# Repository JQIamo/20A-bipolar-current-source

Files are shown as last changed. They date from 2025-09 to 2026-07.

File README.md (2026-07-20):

# Bias Coils Current Controller
This repo provides information regarding the Bias Coils Current Controller (here on out referred to as “the controller”) used by the Schine Group at the Joint Quantum Institute (JQI) at University of Maryland, College Park. This is an experimental apparatus designed to drive Helmholtz coil pairs to cancel external magnetic fields which would otherwise disturb the experiment. The controller provides an output current proportional to an input voltage and features an ultra-low noise feedback circuit design for precise control of the output current down to the fractional mA level. The controller has three channels to independently control the magnetic fields along the x, y, and z axes.

## 20A-bipolar-current-source
This project is based on the [`20A-bipolar-current-source`](https://github.com/JQIamo/20A-bipolar-current-source/tree/faf83a785aa46d90d6e65fa55f9879bae6bd2d8a) design of Mingshu Zhao and Alessandro Restelli. Details on the circuit can be found in their [research article in AIP Advances](https://doi.org/10.1063/5.0138145).

## Circuit files
There are several KiCad project folders within the `kicad` directory in this repo.
* `controller_board` contains the circuit board for the main controller board on which the analog PI feedback is located.
* `Controller_supply` contains the controller's on-board power supply circuit board (used for powering the controller boards)
* `H-bridge` is for the development of the MOT coil current controller (empty project as of Jun 06, 2024).
* `rear` contains the original, liquid-cooled circuit board design housing the power MOSFETs that control the coil current. (Not used in this controller)
* `SchineLab_CoilFET_Board` contains the modified, air-cooled circuit board design housing the power MOSFETs for coil current control. (Used in this controller)

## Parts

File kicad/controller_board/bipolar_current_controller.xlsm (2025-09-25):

# | Reference | Qty | Value | Footprint | DNP | DIGIKEY PARTNO | MPN
1 | C1, C2, C3, C4, C5, C6, C7, C8, C9, C10, C11, C12, C13, C14, C15, C16, C17, C18, C19, C20, C22, C23, C37, C43, C44, C47, C48 | 27 | 0.1uF | Capacitor_SMD:C_0603_1608Metric |  | 490-14357-1-ND | GCM188R71H104JA57D
2 | C24, C29 | 2 | 10n | Capacitor_SMD:C_0603_1608Metric |  | 445-7404-1-ND | C1608C0G1H103J080AA
3 | C25, C27, C28, C30 | 4 | 1n | Capacitor_SMD:C_0603_1608Metric |  | 1276-1018-1-ND | 1276-1018-1-ND
4 | C31, C32 | 2 | 220uF | zmyfootprint:CAP_polar_220uF |  | PCE4428CT-ND | EEE-FK1V221AP
5 | C33, C34, C39, C40, C49, C51 | 6 | 10uF | Capacitor_SMD:C_1210_3225Metric |  | 445-14933-1-ND | C3225X7R1H106M250AC
6 | C35, C36 | 2 | 47uF | Capacitor_Tantalum_SMD:CP_EIA-7343-43_Kemet-X |  | 399-3905-1-ND | T495X476K035ATE300
7 | C41, C42, C45, C46 | 4 | 0.33uF | Capacitor_SMD:C_0603_1608Metric |  | 445-5950-1-ND | C1608X7R1H334K080AC
8 | C50, C52 | 2 | 1uF | Capacitor_Tantalum_SMD:CP_EIA-3528-21_Kemet-B |  | 399-9720-1-ND | T491B105K050AT
9 | D1, D2, D4, D5 | 4 | D | Diode_SMD:D_MiniMELF |  | 1514-CLL4150TRPBFREECT-ND | CLL4150 TR PBFREE
10 | D3, D6 | 2 | LED | LED_THT:LED_D5.0mm_Horizontal_O3.81mm_Z3.0mm |  | 516-2483-1-ND | HLMP-4700-C0002
11 | H1, H2, H3, H4 | 4 | MountingHole | MountingHole:MountingHole_4mm
12 | J1 | 1 | Error signal | zKiCadFootprints:BNC_Amphenol_B6252HB-NPP3G-50_Horizontal_mount_float |  | A32260-ND | 5227161-7
13 | J2 | 1 | Set point | zKiCadFootprints:BNC_Amphenol_B6252HB-NPP3G-50_Horizontal_mount_float |  | A32260-ND | 5227161-7
14 | J4 | 1 | Monitor | zKiCadFootprints:BNC_Amphenol_B6252HB-NPP3G-50_Horizontal_mount_float |  | A32260-ND | 5227161-7
15 | J5 | 1 | Conn_02x04_Counter_Clockwise | zKiCadFootprints:SSO-8_7.62x10.1mm_P2.54mm_Clearance8mm |  | 1212-1032-ND | 114-87-308-41-134161
16 | J6 | 1 | Enable | zKiCadFootprints:BNC_Amphenol_B6252HB-NPP3G-50_Horizontal_mount_float |  | A32260-ND | 5227161-7
17 | J7 | 1 | N-MOS | Connector_Molex:Molex_KK-254_AE-6410-02A_1x02_P2.54mm_Vertical
18 | J8 | 1 | P-MOS | Connector_Molex:Molex_KK-254_AE-6410-02A_1x02_P2.54mm_Vertical
19 | J9 | 1 | Shunt resistor | Connector_Molex:Molex_KK-254_AE-6410-02A_1x02_P2.54mm_Vertical
20 | L1, L2 | 2 | 100uH | Inductor_SMD:L_TDK_SLF10145 |  | 445-1976-1-ND | SLF10145T-101M1R0-PF
21 | L3, L4 | 2 | 1k | Inductor_SMD:L_0603_1608Metric |  | 445-MMZ1608R102ATA00CT-ND | MMZ1608R102ATA00
22 | P1 | 1 | CONN_01X03 | zmyfootprint:Conn_01X03-3.5mm |  | 277-1722-ND | 1984620
23 | R1, R3, R10 | 3 | 50 | Resistor_SMD:R_0603_1608Metric |  | 764-FC0603E50R0BTBST1CT-ND | FC0603E50R0BTBST1
24 | R2 | 1 | 200 | Resistor_SMD:R_0603_1608Metric |  | RNCF0603TKY200RCT-ND | RNCF0603TKY200R
25 | R4 | 1 | 1M | Resistor_SMD:R_0603_1608Metric |  | YAG4498CT-ND | RT0603BRD071ML
26 | R5 | 1 | DNP | Resistor_SMD:R_0805_2012Metric
27 | R6 | 1 | 1k | Resistor_SMD:R_0805_2012Metric |  | RG2012V1.0KPCT-ND | RNCF0805TKY1K00
28 | R7 | 1 | R_Shunt |  |  | 804-1050-ND | Y09430R01000F9L
29 | R8, R11 | 2 | 25k | Resistor_SMD:R_2512_6332Metric |  | 804-1122-1-ND | Y174525K0000T9R
30 | R9, R12 | 2 | 500 | Resistor_SMD:R_2512_6332Metric |  | Y1121-500CT-ND | Y1121500R000T9R
31 | R13, R15, R17, R18 | 4 | 18.2k | Resistor_SMD:R_0805_2012Metric |  | 2019-RK73H2ATTD1822FCT-ND | RK73H2ATTD1822F
32 | R14, R16, R19, R20 | 4 | 2.2k | Resistor_SMD:R_0805_2012Metric |  | 749-1728-1-ND | MCU08050C2201FP500
33 | R22, R23 | 2 | 1 | Resistor_SMD:R_0603_1608Metric |  | RNCP0603FTD1R00CT-ND | RNCP0603FTD1R00
34 | R25, R26 | 2 | DNP | Resistor_SMD:R_0603_1608Metric
35 | R27, R28 | 2 | 33 | Resistor_SMD:R_0603_1608Metric |  | 311-33.0HRCT-ND | RC0603FR-0733RL
36 | R31, R32, R39 | 3 | 1k | Resistor_SMD:R_0603_1608Metric |  | RNCP0603FTD1K00CT-ND | RNCP0603FTD1K00
37 | R33, R34 | 2 | 1.8k | Resistor_SMD:R_0603_1608Metric |  | 764-1393-1-ND | PTN0603E1801BST1
38 | R35, R36, R37, R38 | 4 | 120 | Resistor_SMD:R_0603_1608Metric |  | RG16P120BCT-ND | RG1608P-121-B-T5
39 | R40, R41 | 2 | 30m | Resistor_SMD:R_1206_3216Metric |  | 4463-D1WEL1206MR033F-T5CT-ND | D1WEL1206MR033F-T5
40 | RV1, RV2 | 2 | 1k | Potentiometer_THT:Potentiometer_Bourns_3296W_Vertical |  | 3296W-102LF-ND | 3296W-1-102LF
41 | S1, S2 | 2 | MAX4656 | zKiCadFootprints:MAX4656ESA+ |  | MAX4656ESA+-ND | MAX4656ESA+
42 | TP1 | 1 | TestPoint_Small | RF_Shielding:Laird_Technologies_BMI-S-210-F_44.00x30.50mm |  | 903-1057-1-ND and 903-1020-ND | BMI-S-210-F and BMI-S-210-C
43 | U1, U2, U3 | 3 | AD8421 | zKiCadFootprints:AD8421ARZ-R7 |  | AD8421ARZ-R7CT-ND | AD8421ARZ-R7
44 | U4 | 1 | OPA388 | zKiCadFootprints:OPA388IDR |  | 296-45348-1-ND | OPA388IDR
45 | U5, U6 | 2 | LT1363 | zKiCadFootprints:LT1363CS8#TRPBF |  | 505-LT1363CS8#TRPBFCT-ND | LT1363CS8#TRPBF
46 | U7, U8 | 2 | BUF634A | zKiCadFootprints:TI_SO-PowerPAD-8_ThermalVias |  | 296-BUF634AIDDARCT-ND | BUF634AIDDAR
47 | U11 | 1 | LM338 | Package_TO_SOT_THT:TO-220-3_Vertical |  | LM338T/NOPB-ND | LM338T/NOPB
48 | U12 | 1 | LM337_TO220 | Package_TO_SOT_THT:TO-220-3_Vertical |  | 497-1585-5-ND | LM337SP
49 | U13 | 1 | LM7915 | Package_TO_SOT_SMD:TO-263-2 |  | MC7915ACD2TGOS-ND | MC7915ACD2TG
50 | U14 | 1 | uA7815 | Package_TO_SOT_SMD:TO-252-2 |  | BA7815FP-E2CT-ND | BA7815FP-E2
51 | U15 | 1 | LM7905 | Package_TO_SOT_SMD:TO-263-2 |  | 497-1214-1-ND | L7905CD2T-TR
52 | U16 | 1 | LM7805 | Package_TO_SOT_SMD:TO-263-3_TabPin2 |  | 296-20796-1-ND | UA7805CKTTR
53 | U17 | 1 | TL1963A | zKiCadFootprints:TL1963ADCQR |  | 296-25119-1-ND | TL1963ADCQR
54 | U18 | 1 | LM337_TO220 | Package_TO_SOT_SMD:TO-263-3_TabPin2 |  | 296-20746-1-ND | LM337KTTR
55 | U19 | 1 | FOD8482TR2 | Package_SO:SSO-6_6.8x4.6mm_P1.27mm_Clearance8mm |  | 488-FOD8482TR2CT-ND | FOD8482TR2

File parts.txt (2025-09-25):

[H-Bridge Parts]
N-MOS : https://www.digikey.com/en/products/detail/infineon-technologies/IAUT300N10S5N014ATMA1/15776582?s=N4IgTCBcDaICxwBwFoCSBBAqgFQMwAZ8A5ARnwGUBWI-EudbAWXRIGFtkiAREAXQF8gA
    - Quantity : 4
    - Manf Part No : IAUT300N10S5N014ATMA1
    - Digikey Part No : 448-IAUT300N10S5N014ATMA1CT-ND
    - DataSheet : https://www.infineon.com/dgdl/Infineon-IAUT300N10S5N014-DataSheet-v01_01-EN.pdf?fileId=5546d46277921c32017795c1685a4680
H-Bridge-Driver : https://www.digikey.com/en/products/detail/renesas-electronics-corporation/HIP4080AIBZT/1034529
    - Quantity : 1
    - Manf Part No : HIP4080AIBZT
    - Digikey Part No : HIP4080AIBZTCT-ND
    - DataSheet : https://www.renesas.com/en/document/dst/hip4080a-datasheet
Comparator : https://www.digikey.com/en/products/detail/analog-devices-inc/LT1011CS8-PBF/889214
    - Quantity : 1
    - Manf Part No : LT1011CS8#PBF
    - Digikey Part No : LT1011CS8#PBF-ND
    - DataSheet : https://www.analog.com/media/en/technical-documentation/data-sheets/LT1011.pdf
Latch : https://www.digikey.com/en/products/detail/texas-instruments/SN74LVC1G373DCKR/863611'
    - Quantity : 1
    - Manf Part No : SN74LVC1G373DCKR
    - Digikey Part No : 296-18775-1-ND
    - DataSheet : https://www.ti.com/lit/ds/symlink/sn74lvc1g373.pdf?HQS=dis-dk-null-digikeymode-dsf-pf-null-wwe&ts=1747274681390&ref_url=https%253A%252F%252Fwww.ti.com%252Fgeneral%252Fdocs%252Fsuppproductinfo.tsp%253FdistId%253D10%2526gotoUrl%253Dhttps%253A%252F%252Fwww.ti.com%252Flit%252Fgpn%252Fsn74lvc1g373
Inverter : https://www.digikey.com/en/products/detail/texas-instruments/SN74AC14DR/376434
    - Quantity : 1
    - Manf Part No : SN74AC14DR
    - Digikey Part No : 296-4300-1-ND
    - DataSheet : https://www.ti.com/lit/ds/symlink/sn74ac14.pdf?HQS=dis-dk-null-digikeymode-dsf-pf-null-wwe&ts=1747274728530&ref_url=https%253A%252F%252Fwww.ti.com%252Fgeneral%252Fdocs%252Fsuppproductinfo.tsp%253FdistId%253D10%2526gotoUrl%253Dhttps%253A%252F%252Fwww.ti.com%252Flit%252Fgpn%252Fsn74ac14
DC-DC Converter: https://www.digikey.com/en/products/detail/cui-inc/PDS1-S15-S15-M/5277662
    - Quantity : 1
    - Manf Part No : PDS1-S15-S15-M
    - Digikey Part No : 102-4546-ND
    - DataSheet : https://www.belfuse.com/media/datasheets/products/power-supplies/PDS1-M.pdf
Voltage Regulator : https://www.digikey.com/en/products/detail/texas-instruments/lm340mpx-5-0-nopb/367021
    - Quantity : 1
    - Manf Part No : LM340MPX-5.0/NOPB
    - Digikey Part No : LM340MPX-5.0/NOPBCT-ND
    - DataSheet : https://www.ti.com/lit/ds/symlink/lm7800.pdf
80V Varistor : https://www.digikey.com/en/products/detail/littelfuse-inc/V20E50P/5290472
    - Quantity : 1
    - Manf Part No : V20E50P
    - Digikey Part No : F6901-ND
    - DataSheet : https://www.littelfuse.com/assetdocs/littelfuse_varistor_lv_ultramov_datasheet.pdf?assetguid=293ecf97-62b0-4b10-a8a2-65c9fb8c7295
Rectifier Diodes : https://www.digikey.com/en/products/detail/nexperia-usa-inc/PMEG10020AELRX/5395777?s=N4IgTCBcDaIAoFkCiBxAjABg2DBBJAMgEoAaIAugL5A
    - Quantity : 2
    - Manf Part No : PMEG10020AELRX
    - Digikey Part No : 1727-2283-1-ND
    - DataSheet : https://assets.nexperia.com/documents/data-sheet/PMEG10020AELR.pdf
0.047uF Capacitor : https://www.digikey.com/en/products/detail/kemet/C0805C473K2RECAUTO/8646749?s=N4IgTCBcDaIMwE4EFoDCAGAHOgrKgLAOxwDSYASgKKoCCAqgCoDyqDyAcgCIgC6AvkA
    - Quantity : 2
    - Manf Part No : C0805C473K2RECAUTO
    - Digikey Part No : 399-C0805C473K2RECAUTOCT-ND
    - DataSheet : https://content.kemet.com/datasheets/KEM_C1090_X7R_ESD.pdf
0.1uF Capacitor : https://www.digikey.com/en/products/detail/yageo/CC0805KRX7R9BB104/302874
    - Quantity : 11
    - Manf Part No : CC0805KRX7R9BB104
    - Digikey Part No : 311-1140-1-ND
    - DataSheet : https://www.yageo.com/upload/media/product/productsearch/datasheet/mlcc/UPY-GPHC_X7R_6.3V-to-250V_24.pdf
22uF Capacitor : https://www.digikey.com/en/products/detail/tdk-corporation/C2012X5R1V226M125AC/3951664
    - Quantity : 4
    - Manf Part No : C2012X5R1V226M125AC
    - Digikey Part No : 445-14428-1-ND
    - DataSheet : https://product.tdk.com/system/files/dam/doc/product/capacitor/ceramic/mlcc/catalog/mlcc_commercial_general_en.pdf
0 Ohms Resistor : https://www.digikey.com/en/products/detail/te-connectivity-passive-product/CRG0805ZR/2380959
    - Quantity : 6
    - Manf Part No : CRG0805ZR
    - Digikey Part No : A106066CT-ND
    - DataSheet : https://www.te.com/usa-en/product-1623401-1.datasheet.pdf
220 Ohms Resistor : https://www.digikey.com/en/products/detail/te-connectivity-passive-product/CRGCQ0805F220R/8576343
    - Quantity : 1
    - Manf Part No : CRGCQ0805F220R
    - Digikey Part No : A129741CT-ND
    - DataSheet : https://www.te.com/usa-en/product-1-2176341-7.datasheet.pdf
330 Ohms Resistor : https://www.digikey.com/en/products/detail/te-connectivity-passive-product/CRGCQ0805F330R/8576345
    - Quantity : 2
    - Manf Part No : CRGCQ0805F330R
    - Digikey Part No : A129743CT-ND
    - DataSheet : https://www.te.com/usa-en/product-1-2176341-9.datasheet.pdf
10kOhms Resistor : https://www.digikey.com/en/products/detail/te-connectivity-passive-product/CRGCQ0805F10K/8576363
    - Quantity : 5
    - Manf Part No : CRGCQ0805F10K
    - Digikey Part No : A129761CT-ND
    - DataSheet : https://www.te.com/usa-en/product-3-2176341-7.datasheet.pdf
100kOhms Resistor : https://www.digikey.com/en/products/detail/te-connectivity-passive-product/CRG0805F100K/2380829
    - Quantity : 2
    - Manf Part No : CRG0805F100K
    - Digikey Part No : A106052CT-ND
    - DataSheet : https://www.te.com/usa-en/product-1623095-1.datasheet.pdf
100kOhms Potentiometer : https://www.digikey.com/en/products/detail/bourns-inc/3266Y-1-104LF/2535462?s=N4IgTCBcDaIMxgGyIJoFoCMmAMAWAMgGJoByAIiALoC%2BQA
    - Quantity : 1
    - Manf Part No : 3266Y-1-104LF
    - Digikey Part No : 3266Y-1-104LF-ND
    - DataSheet : https://www.bourns.com/docs/Product-Datasheets/3266.pdf
4.7kOhms Ferrite Bead : https://www.digikey.com/en/products/detail/murata-electronics/BLM21HE472SN1L/17184947?s=N4IgTCBcDaICwE4AMBaAQgGQLJgIwAkBROAdjAGUA5XDAYQBUVKAREAXQF8g
    - Quantity : 5
    - Manf Part No : BLM21HE472SN1L
    - Digikey Part No : 490-BLM21HE472SN1LCT-ND
    - DataSheet : https://www.murata.com/en-us/api/pdfdownloadapi?cate=cgsubChipFerriBead&partno=BLM21HE472SN1%23
Otocoupler : https://www.digikey.com/en/products/detail/liteon/LTV-817/385836
    - Quantity : 1
    - Manf Part No : LTV-817
    - Digikey Part No : 160-1366-5-ND
    - DataSheet : https://optoelectronics.liteon.com/upload/download/DS-70-96-0016/LTV-8X7%20series%20%20Rev.S.PDF
LED : https://www.digikey.com/en/products/detail/kingbright/AA4040R3G2CT-R-10MAT/17969033?s=N4IgjCBcoMwOxVAYygMwIYBsDOBTANCAPZQDaIMArGACxgBMIhVtlCz1NcADExQJyUYANhh8YguuwGUa3MQF1CABwAuUEAGVVAJwCWAOwDmIAL6Fh-RCBSQMOAsTIg6YfvQiE5-GvV5KQNQ1tfWMzQj8EaBs0LDxCEkhyGDc4BhAAoMgtXUMTcxAAWkZo210AV0dE8koM03qgA
    - Quantity : 2
    - Manf Part No : AA4040R3G2CT/R-10MAT
    - Digikey Part No : 754-AA4040R3G2CT/R-10MATCT-ND
    - DataSheet : https://www.kingbrightusa.com/images/catalog/SPEC/AA4040R3G2CT-R-10MAT.pdf
Light Pipes : https://www.digikey.com/en/products/detail/dialight/51513020125F/4965188
    - Quantity : 2
    - Manf Part No : 51513020125F
    - Digikey Part No : 350-3733-ND
    - DataSheet : https://s3-us-west-2.amazonaws.com/catsy.557/Dialight_datasheet_515_VPM_3mm.pdf
Screw Terminal 0x2 : https://www.digikey.com/en/products/detail/phoenix-contact/1984617/950849?s=N4IgTCBcDa4OxwLQEY5mYgcgERAXQF8g2
    - Quantity : 1
    - Manf Part No : 1984617
    - Digikey Part No : 277-1721-ND
    - DataSheet : https://mm.digikey.com/Volume0/opasdata/d220001/medias/docus/2450/Combicon%20Compact%20Series.pdf
Screw Terminal 0x3 : https://www.digikey.com/en/products/detail/phoenix-contact/1984620/950850?s=N4IgTCBcDa4OxwLQEY5jIgcgERAXQF8g
    - Quantity : 1
    - Manf Part No : 1984620
    - Digikey Part No : 277-1722-ND
    - DataSheet : https://mm.digikey.com/Volume0/opasdata/d220001/medias/docus/2450/Combicon%20Compact%20Series.pdf
Terminal BLock 0x4 : https://www.digikey.com/en/products/detail/weidm%C3%BCller/2453710000/9637692?s=N4IgTCBcDa4CwFYDMB2AjABixkBdAvkA
    - Quantity : 1
    - Manf Part No : 2453710000
    - Digikey Part No : 2453710000-ND
    - DataSheet : https://mm.digikey.com/Volume0/opasdata/d220001/medias/docus/565/2453710000_DS.pdf
BNC Connector Jack, Female Socket  : https://www.digikey.com/en/products/detail/te-connectivity-amp-connectors/5227161-7/811158?s=N4IgTCBcDaIIIGYxgGwAYC0A5AIiAugL5A
    - Quantity : 1
    - Manf Part No : 5227161-7
    - Digikey Part No : A32260-ND
    - DataSheet : https://www.te.com/usa-en/product-5227161-7.datasheet.pdf

[Relay Board Parts]
Mechanical Relays : https://www.digikey.com/en/products/detail/cit-relay-and-switch/J115F11CH24VDCS61-5U/12502937?s=N4IgTCBcDa4CxwJwFoBSBGdBWAYpgwgBJhwBqAIvgMoBs6AdFgKrIBy5IAugL5A
    - Quantity : 2
    - Manf Part No : J115F11CH24VDCS61.5U
    - Digikey Part No : 2449-J115F11CH24VDCS61.5U-ND
    - DataSheet : https://www.citrelay.com/Catalog%20Pages/RelayCatalog/J115F%2050amp.pdf
Rectifier Diode : https://www.digikey.com/en/products/detail/smc-diode-solutions/1N5400/5993023?s=N4IgTCBcDaIIwDYCsSC0cBySAsAGXAKgEKoYAiIAugL5A
    - Quantity : 1
    - Manf Part No : 1N5400
    - Digikey Part No : 1655-1N5400TB-ND
    - DataSheet : https://www.smc-diodes.com/propdf/1N5400-1N5408%20N0547%20REV.A.pdf
470 Ohms 10W Power Resistor : https://www.digikey.com/en/products/detail/te-connectivity-passive-product/SQPW10470RJ/2365771?s=N4IgTCBcDaIIIEYDMB2ALAgHAWgHIBEQBdAXyA
    - Quantity : 1
    - Manf Part No : SQPW10470RJ
    - Digikey Part No : A137418-ND
    - DataSheet : https://www.te.com/usa-en/product-1-1623795-1.datasheet.pdf
220 µF Electrolytic Capacitors : https://www.digikey.com/en/products/detail/nichicon/UVP1H221MHD1TO/4328902?s=N4IgTCBcDaICwE4DMBaAjGA7ABjelAcgCIgC6AvkA
    - Quantity : 1
    - Manf Part No : UVP1H221MHD1TO
    - Digikey Part No : 493-12701-1-ND
    - DataSheet : https://products.nichicon.co.jp/en/pdf/XJA043/e-uvp.pdf
Screw Terminal 0x2 : https://www.digikey.com/en/products/detail/phoenix-contact/1984617/950849?s=N4IgTCBcDa4OxwLQEY5mYgcgERAXQF8g2
    - Quantity : 1
    - Manf Part No : 1984617
    - Digikey Part No : 277-1721-ND
    - DataSheet : https://mm.digikey.com/Volume0/opasdata/d220001/medias/docus/2450/Combicon%20Compact%20Series.pdf
Terminal BLock 0x4 : https://www.digikey.com/en/products/detail/weidm%C3%BCller/2453710000/9637692?s=N4IgTCBcDa4CwFYDMB2AjABixkBdAvkA
    - Quantity : 1
    - Manf Part No : 2453710000
    - Digikey Part No : 2453710000-ND
    - DataSheet : https://mm.digikey.com/Volume0/opasdata/d220001/medias/docus/565/2453710000_DS.pdf

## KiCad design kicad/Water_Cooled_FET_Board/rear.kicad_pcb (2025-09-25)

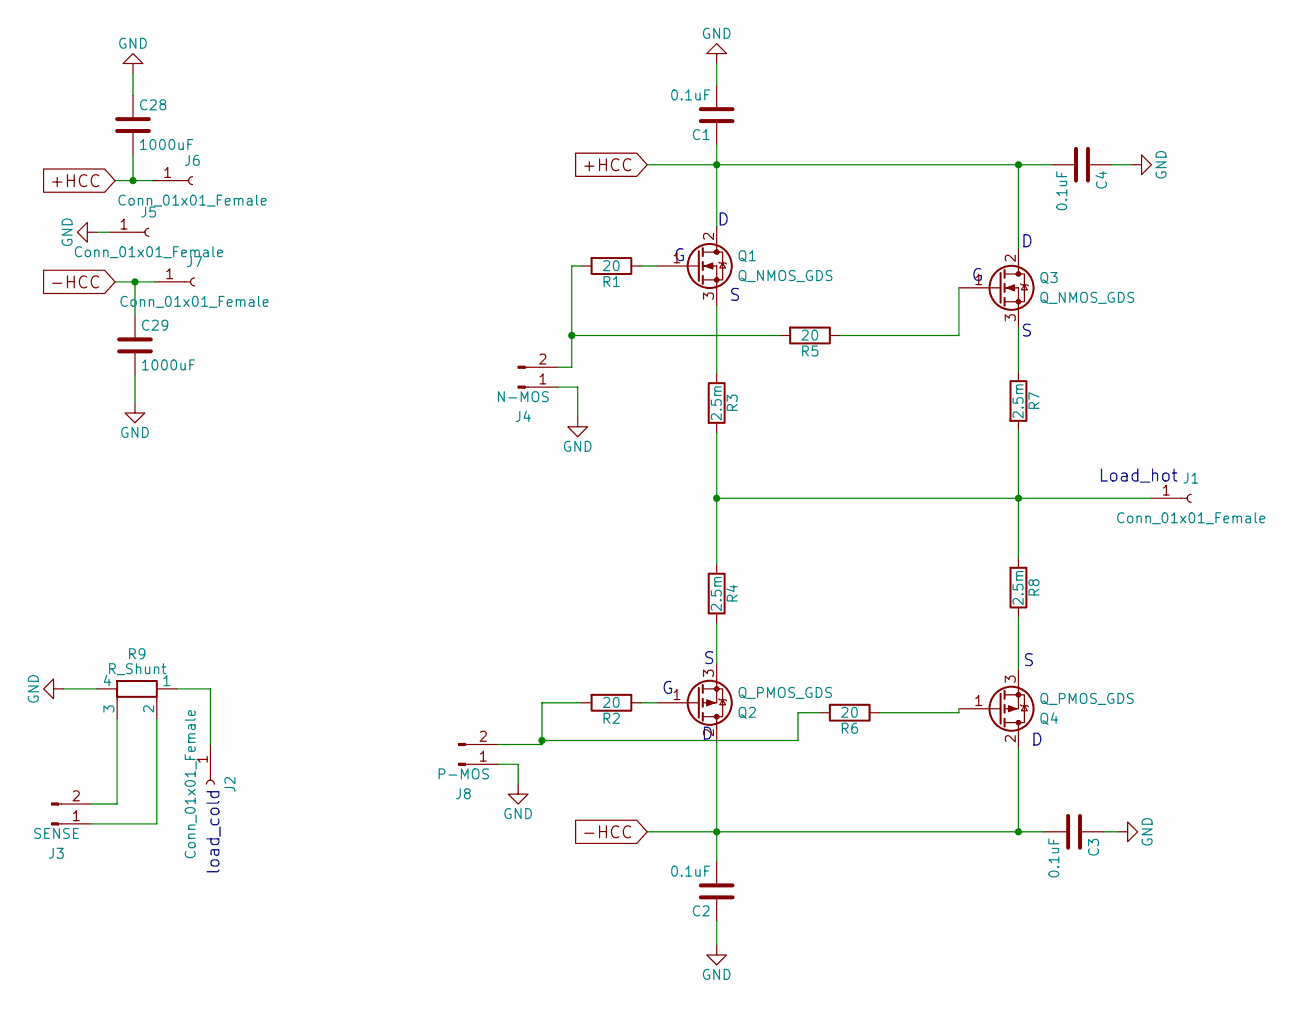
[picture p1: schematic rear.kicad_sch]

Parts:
C1, C2, C3, C4: 0.1uF; C_0603; MPN C0603C104J5RACAUTO; DIGIKEY PARTNO 399-6853-1-ND
C28, C29: 1000uF; CAPCITOR_TOT; DIGIKEY PARTNO 647-UKL1J102KHD
J1, J2, J5, J6, J7: Conn_01x01_Female; SAFETY-BANANA-JACK-CT3151
J3: SENSE; PinHeader_1x02_P2.54mm_Vertical
J4: N-MOS; PinHeader_1x02_P2.54mm_Vertical
J8: P-MOS; PinHeader_1x02_P2.54mm_Vertical
Q1, Q3: Q_NMOS_GDS; PowerMOS; DIGIKEY PARTNO IXFN520N075T2-ND
Q2, Q4: Q_PMOS_GDS; PowerMOS; DIGIKEY PARTNO IXTN170P10P-ND
R1, R2, R5, R6: 20; R_0603_1608Metric_Pad0.98x0.95mm_HandSolder; DIGIKEY PARTNO P20.00BYCT-ND
R3, R4, R7, R8: 2.5m; R_2512; DIGIKEY PARTNO A129569CT-ND
R9: R_Shunt; SHR4-3825

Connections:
+HCC: C1.1, C4.2, C28.2, J6.1, Q1.2 (D), Q3.2 (D)
-HCC: C2.2, C3.2, C29.1, J7.1, Q2.2 (D), Q4.2 (D)
GND: C1.2, C2.1, C3.1, C4.1, C28.1, C29.2, J4.1, J5.1, J8.1, R9.4
unnamed: J1.1, R3.2, R4.2, R7.2, R8.2
unnamed: J2.1, R9.1
unnamed: J3.1, R9.2
unnamed: J3.2, R9.3
unnamed: J4.2, R1.2, R5.2
unnamed: J8.2, R2.2, R6.2
unnamed: Q1.1 (G), R1.1
unnamed: Q1.3 (S), R3.1
unnamed: Q2.1 (G), R2.1
unnamed: Q2.3 (S), R4.1
unnamed: Q3.1 (G), R5.1
unnamed: Q3.3 (S), R7.1
unnamed: Q4.1 (G), R6.1
unnamed: Q4.3 (S), R8.1

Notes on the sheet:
load_cold
Load_hot

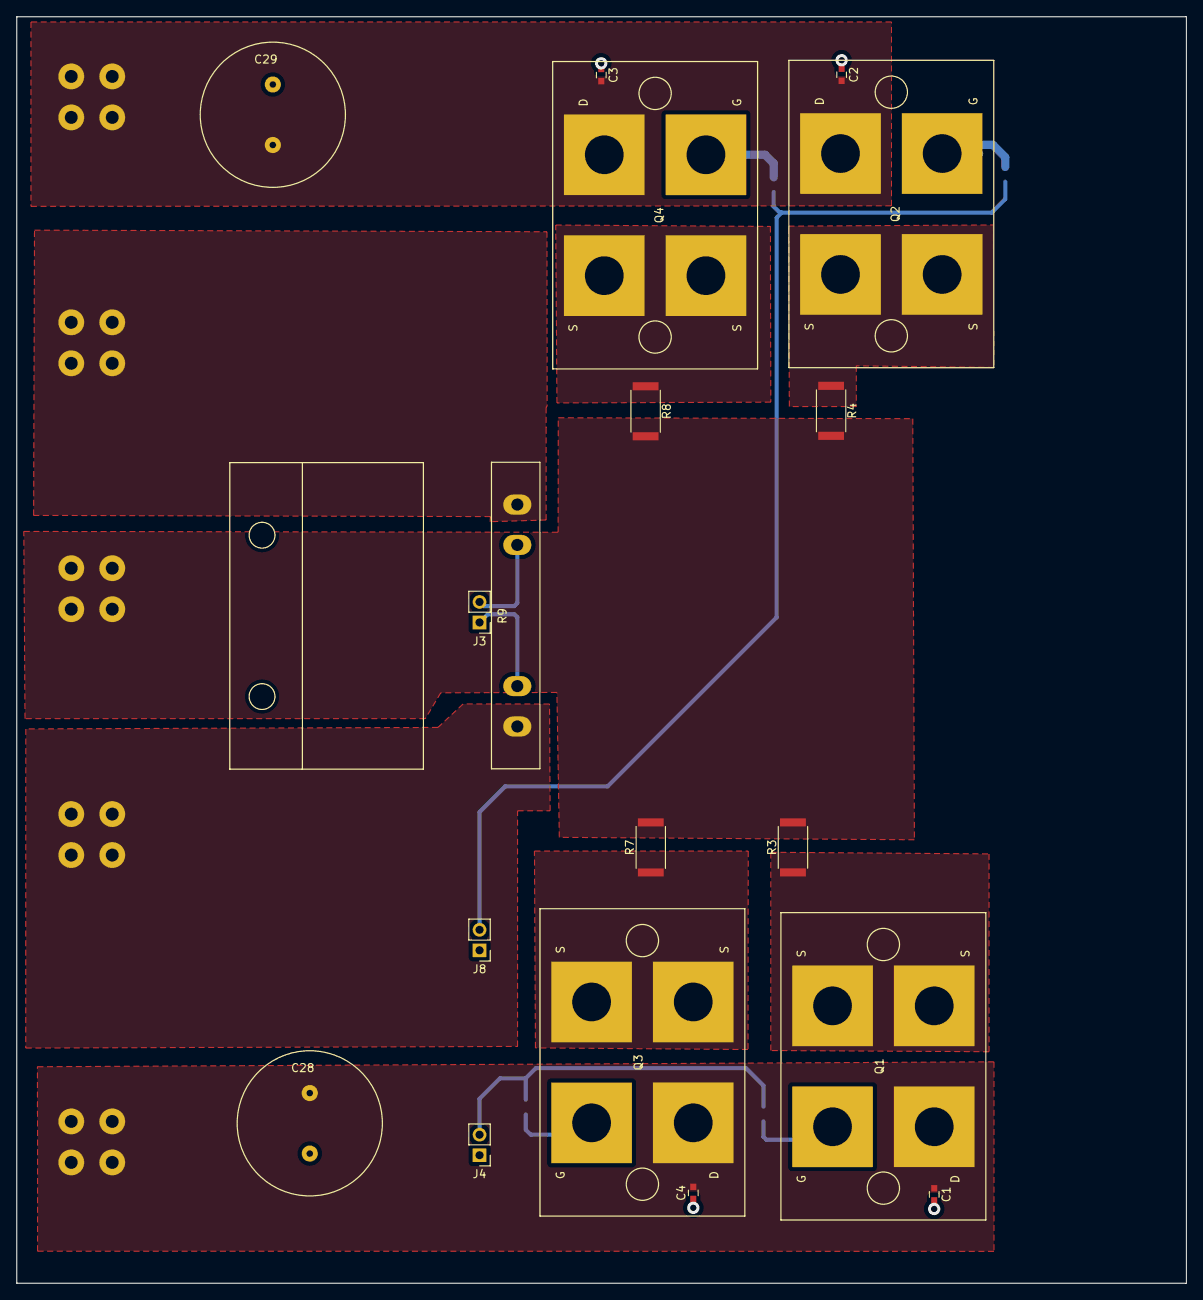
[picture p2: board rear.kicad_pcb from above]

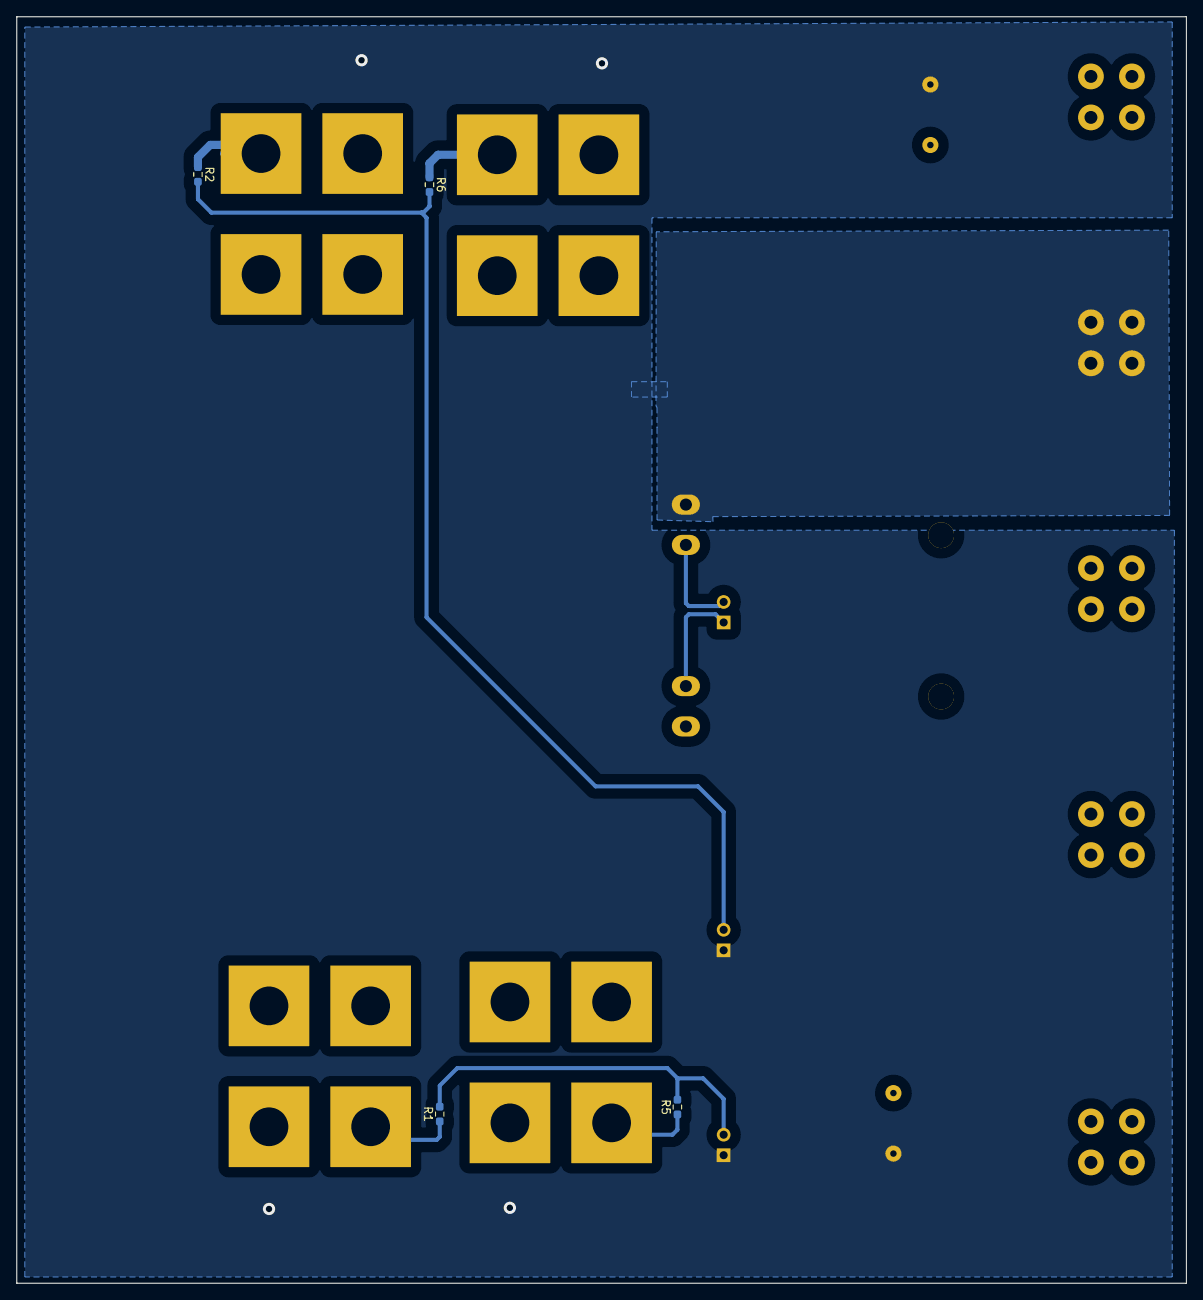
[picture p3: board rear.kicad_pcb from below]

Board: 2 copper layers, 145.0 x 157.0 mm, 27 parts (4 on the bottom side), 17 nets.

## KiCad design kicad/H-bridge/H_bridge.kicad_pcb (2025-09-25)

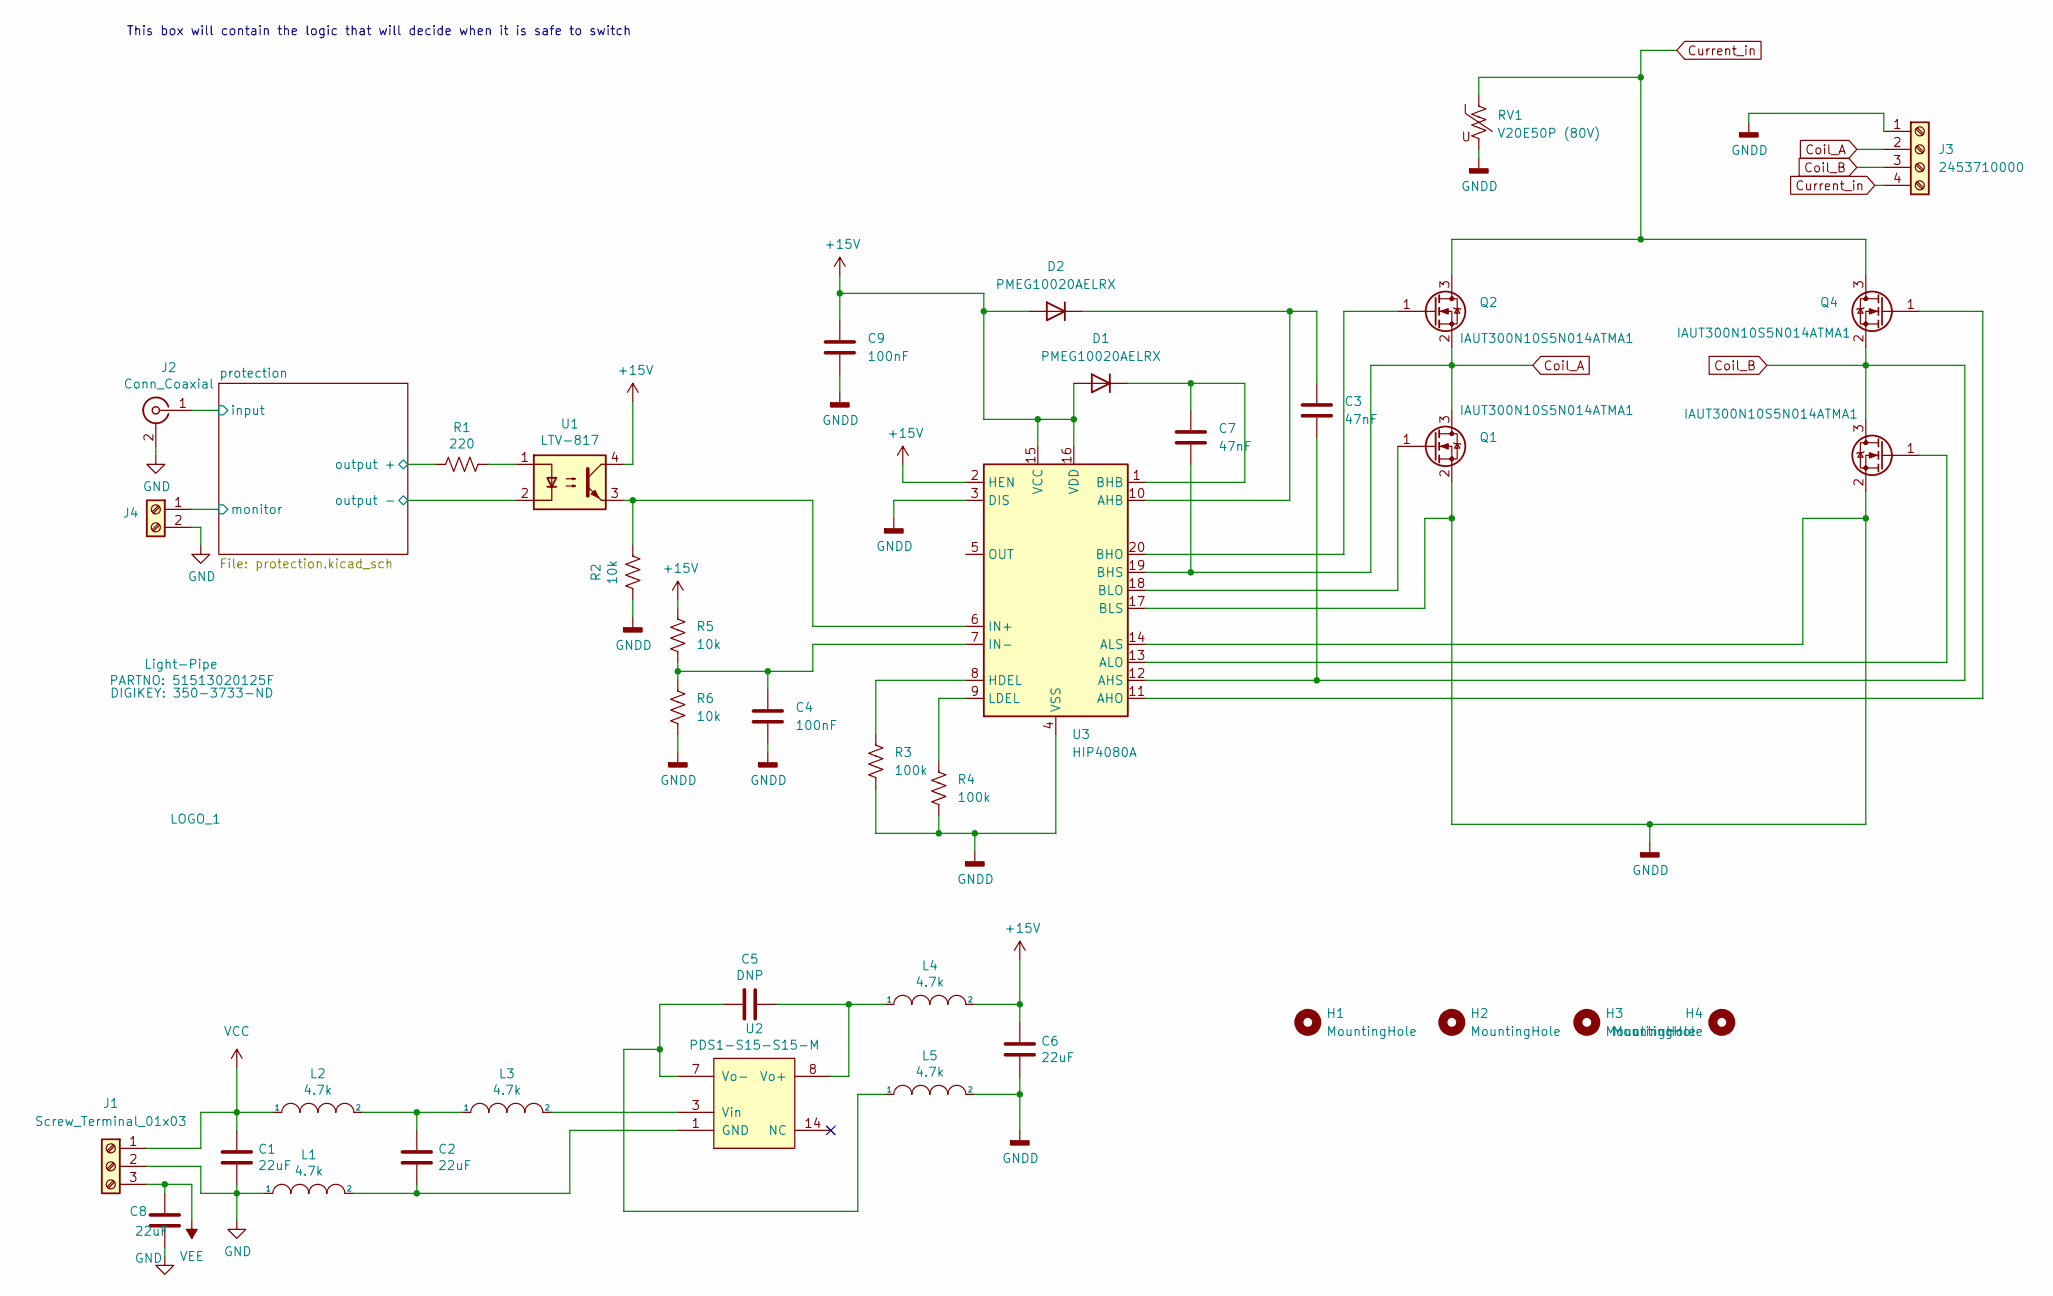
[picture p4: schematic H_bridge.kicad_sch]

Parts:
BOM1: Light-Pipe; PARTNO 51513020125F; DIGIKEY 350-3733-ND
C1, C2, C6, C8: 22uF; C_0805_2012Metric; PARTNO C2012X5R1V226M125AC; DIGIKEY 445-14428-1-ND
C3, C7: 47nF; C_0805_2012Metric; PARTNO C0805C473K2RECAUTO; DIGIKEY 399-C0805C473K2RECAUTOCT-ND
C4, C9: 100nF; C_0805_2012Metric; PARTNO CC0805KRX7R9BB104; DIGIKEY 311-1140-1-ND
C5: DNP; C_0805_2012Metric
D1, D2: PMEG10020AELRX; Nexperia_CFP3_SOD-123W; PARTNO PMEG10020AELRX; DIGIKEY 1727-2283-1-ND
H1, H2, H3, H4: MountingHole; MountingHole_3.5mm
J1: Screw_Terminal_01x03; TerminalBlock_4Ucon_1x03_P3.50mm_Horizontal; PARTNO 1984620; DIGIKEY 277-1722-ND
J2: Conn_Coaxial; BNC_Socket_TYCO-AMP; PARTNO 5227161-7; DIGIKEY A32260-ND
J3: 2453710000; CONN_2453710000; PARTNO 2453710000; DIGIKEY 2453710000-ND
J4: Screw_Terminal_01x02; TerminalBlock_4Ucon_1x02_P3.50mm_Horizontal; PARTNO 1984617; DIGIKEY 277-1721-ND
L1, L2, L3, L4, L5: 4.7k; L_0805; PARTNO BLM21HE472SN1L; DIGIKEY 490-BLM21HE472SN1LCT-ND
LOGO_1: JQI-Logo
Q1, Q2, Q3, Q4: IAUT300N10S5N014ATMA1; Infineon_PG-HSOF-8-1_ThermalVias; PARTNO IAUT300N10S5N014ATMA1; DIGIKEY 448-IAUT300N10S5N014ATMA1CT-ND
R1: 220; R_0805; PARTNO CRGCQ0805F220R; DIGIKEY A129741CT-ND
R2, R5, R6: 10k; R_0805_2012Metric; PARTNO CRGCQ0805F10K; DIGIKEY A129761CT-ND
R3, R4: 100k; R_0805_2012Metric; PARTNO CRG0805F100K; DIGIKEY A106052CT-ND
RV1: V20E50P (80V); RV_Disc_D15.5mm_W7.5mm_P7.5mm; PARTNO V20E50P; DIGIKEY F6901-ND
U1: LTV-817; DIP-4_W10.16mm_LongPads; PARTNO LTV-817; DIGIKEY 160-1366-5-ND
U2: PDS1-S15-S15-M; DCDC-Conv_muRata_NXE2SxxxxMC; PARTNO PDS1-S15-S15-M; DIGIKEY 102-4546-ND
U3: HIP4080A; SO-20_12.8x7.5mm_P1.27mm; PARTNO HIP4080AIBZT; DIGIKEY HIP4080AIBZTCT-ND

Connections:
+15V: C6.2, C9.1, D1.2 (A), D2.2 (A), L4.2, R5.1, U1.4, U3.2 (HEN), U3.15 (VCC), U3.16 (VDD)
/protection/input: J2.1 (In); also elsewhere on the board
/protection/monitor: J4.1; also elsewhere on the board
/protection/output +: R1.2; also elsewhere on the board
/protection/output -: U1.2; also elsewhere on the board
Coil_A: C7.2, J3.2, Q1.3 (D), Q2.2 (S), U3.19 (BHS)
Coil_B: C3.2, J3.3, Q3.3 (D), Q4.2 (S), U3.12 (AHS)
Current_in: J3.4, Q2.3 (D), Q4.3 (D), RV1.1
GND: C1.2, C8.2, J1.2, J2.2 (Ext), J4.2, L1.1; also elsewhere on the board
GNDD: C4.2, C6.1, C9.2, J3.1, L5.2, Q1.2 (S), Q3.2 (S), R2.2, R3.2, R4.2, R6.2, RV1.2, U3.3 (DIS), U3.4 (VSS), U3.14 (ALS), U3.17 (BLS)
unnamed: C2.1, L2.2, L3.1
unnamed: C7.1, D1.1 (K), U3.1 (BHB)
unnamed: C3.1, D2.1 (K), U3.10 (AHB)
unnamed: Q1.1 (G), U3.18 (BLO)
unnamed: Q2.1 (G), U3.20 (BHO)
unnamed: Q3.1 (G), U3.13 (ALO)
unnamed: Q4.1 (G), U3.11 (AHO)
unnamed: R1.1, U1.1
unnamed: C2.2, L1.2, U2.1 (GND)
unnamed: L3.2, U2.3 (Vin)
unnamed: C5.1, L4.1, U2.8 (Vo+)
unnamed: C5.2, L5.1, U2.7 (Vo-)
unnamed: R3.1, U3.8 (HDEL)
unnamed: R2.1, U1.3, U3.6 (IN+)
unnamed: C4.1, R5.2, R6.1, U3.7 (IN-)
unnamed: R4.1, U3.9 (LDEL)
VCC: C1.1, J1.1, L2.1; also elsewhere on the board
VEE: C8.1, J1.3; also elsewhere on the board

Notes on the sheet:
This box will contain the logic that will decide when it is safe to switch

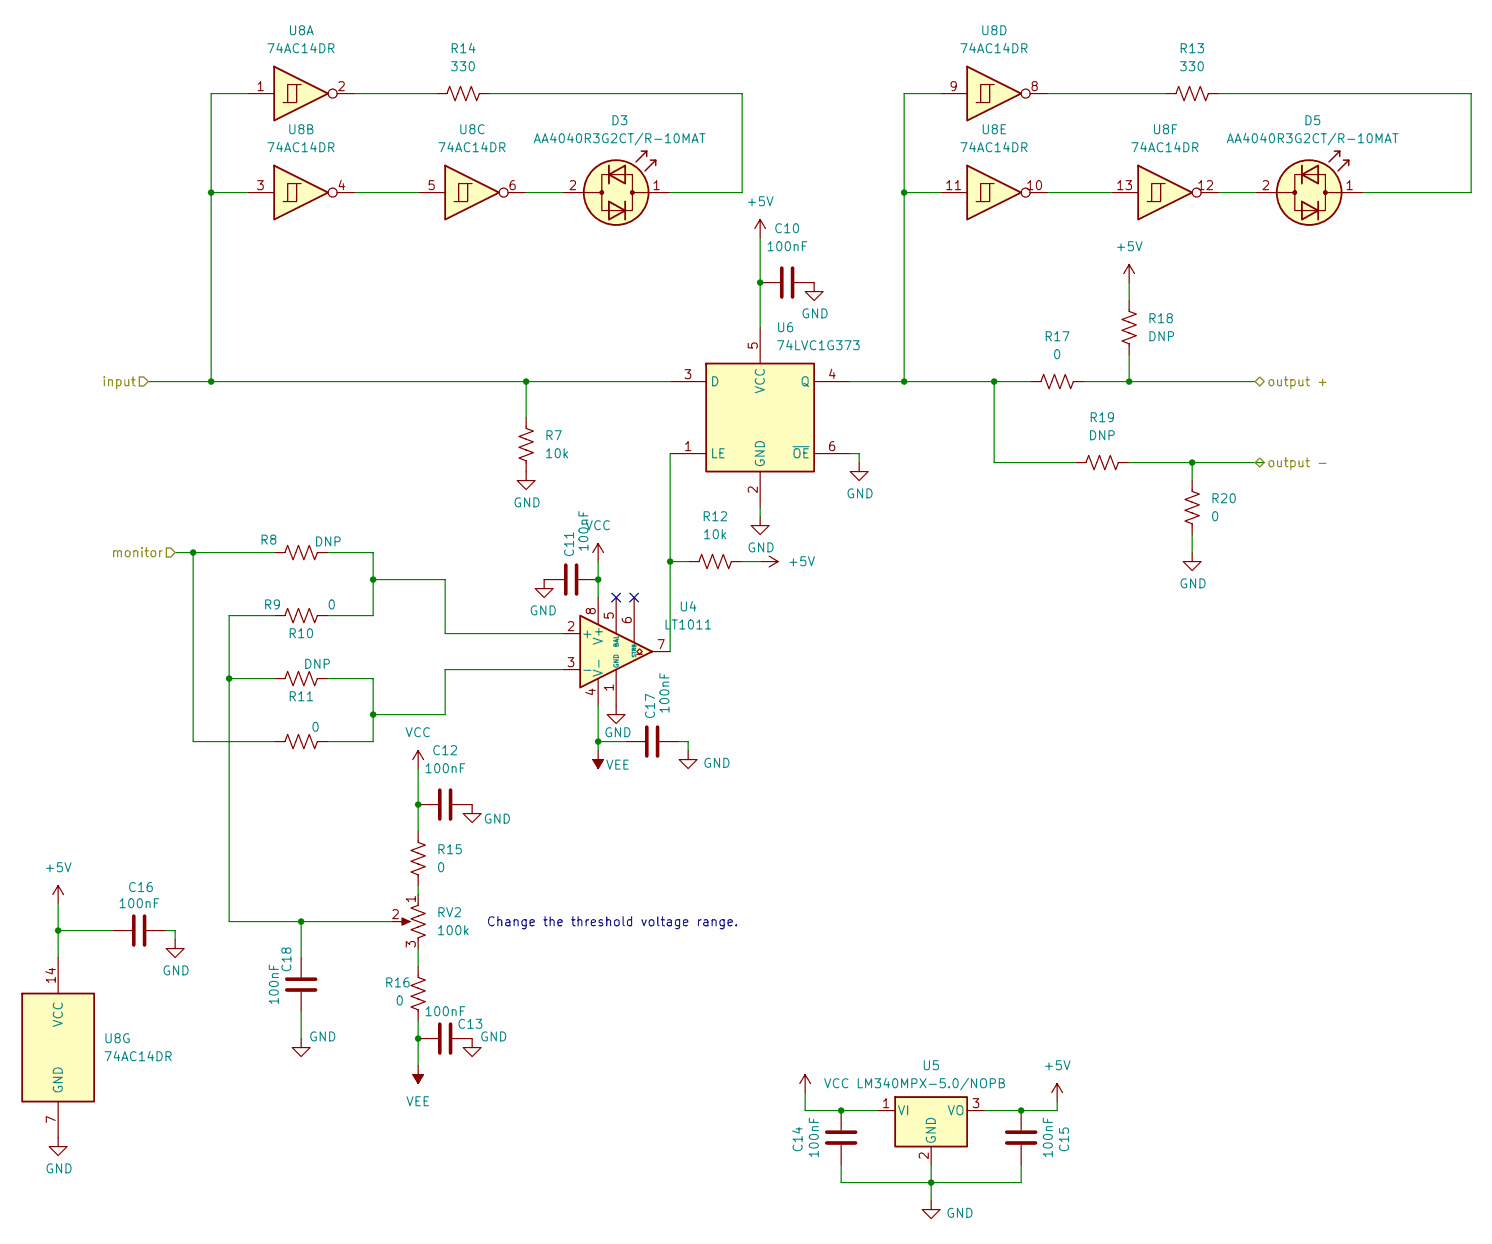
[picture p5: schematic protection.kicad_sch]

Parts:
C10, C11, C12, C13, C14, C15, C16, C17, C18: 100nF; C_0805_2012Metric; PARTNO CC0805KRX7R9BB104; DIGIKEY 311-1140-1-ND
D3, D5: AA4040R3G2CT/R-10MAT; LED_boomerang; PARTNO AA4040R3G2CT/R-10MAT; DIGIKEY 754-AA4040R3G2CT/R-10MATCT-ND
R7, R12: 10k; R_0805_2012Metric; PARTNO CRGCQ0805F10K; DIGIKEY A129761CT-ND
R8, R10, R18, R19: DNP; R_0805_2012Metric
R9, R11, R15, R16, R17, R20: 0; R_0805_2012Metric; PARTNO CRG0805ZR; DIGIKEY A106066CT-ND
R13, R14: 330; R_0805_2012Metric; PARTNO CRGCQ0805F330R; DIGIKEY A129743CT-ND
RV2: 100k; Potentiometer_Bourns_3266Y_Vertical; PARTNO 3266Y-1-104LF; DIGIKEY 3266Y-1-104LF-ND
U4: LT1011; SO-8_3.9x4.9mm_P1.27mm; PARTNO LT1011CS8#PBF; DIGIKEY LT1011CS8#PBF-ND
U5: LM340MPX-5.0/NOPB; SOT-223-3_TabPin2; PARTNO LM340MPX-5.0/NOPB; DIGIKEY LM340MPX-5.0/NOPBCT-ND
U6: 74LVC1G373; SOT-363_SC-70-6; PARTNO SN74LVC1G373DCKR; DIGIKEY 296-18775-1-ND
U8: 74AC14DR; SOIC-14_3.9x8.7mm_P1.27mm; PARTNO SN74AC14DR; DIGIKEY 296-4300-1-ND

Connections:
+5V: C10.1, C15.2, C16.2, R12.2, R18.2, U5.3 (VO), U6.5 (VCC), U8.14 (VCC)
/protection/input: R7.1, U6.3 (D), U8.1, U8.3; also elsewhere on the board
/protection/monitor: R8.1, R11.1; also elsewhere on the board
/protection/output +: R17.2, R18.1; also elsewhere on the board
/protection/output -: R19.1, R20.2; also elsewhere on the board
GND: C10.2, C11.2, C12.2, C13.2, C14.1, C15.1, C16.1, C17.1, C18.1, R7.2, R20.1, U4.1 (GND), U5.2 (GND), U6.2 (GND), U6.6 (~OE), U8.7 (GND); also elsewhere on the board
unnamed: C18.2, R9.1, R10.1, RV2.2
unnamed: D3.2 (AK), U8.6
unnamed: D3.1 (KA), R14.2
unnamed: D5.2 (AK), U8.12
unnamed: D5.1 (KA), R13.2
unnamed: R13.1, U8.8
unnamed: R14.1, U8.2
unnamed: R15.1, RV2.1
unnamed: R16.2, RV2.3
unnamed: R8.2, R9.2, U4.2 (+)
unnamed: R10.2, R11.2, U4.3 (-)
unnamed: R12.1, U4.7, U6.1 (LE)
unnamed: R17.1, R19.2, U6.4 (Q), U8.9, U8.11
unnamed: U8.4, U8.5
unnamed: U8.10, U8.13
VCC: C11.1, C12.1, C14.2, R15.2, U4.8 (V+), U5.1 (VI); also elsewhere on the board
VEE: C13.1, C17.2, R16.1, U4.4 (V-); also elsewhere on the board

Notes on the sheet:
Change the threshold voltage range.

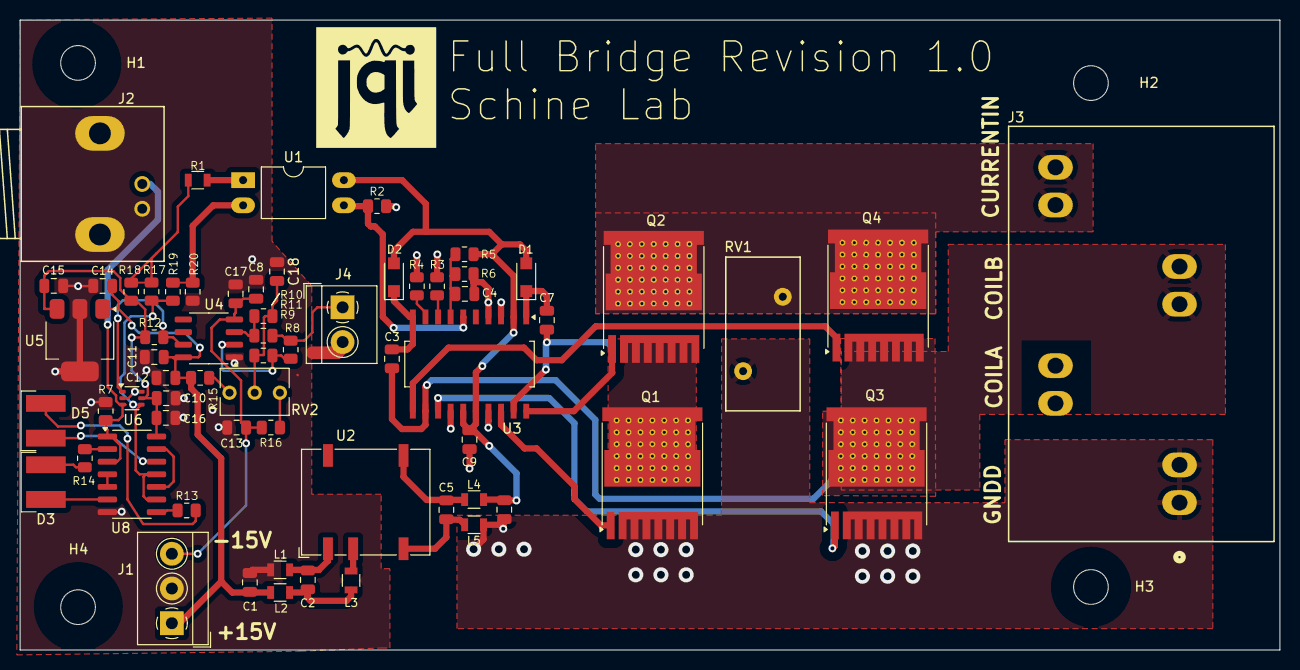
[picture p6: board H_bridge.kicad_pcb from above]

Board: 2 copper layers, 127.0 x 63.5 mm, 69 parts (0 on the bottom side), 44 nets.

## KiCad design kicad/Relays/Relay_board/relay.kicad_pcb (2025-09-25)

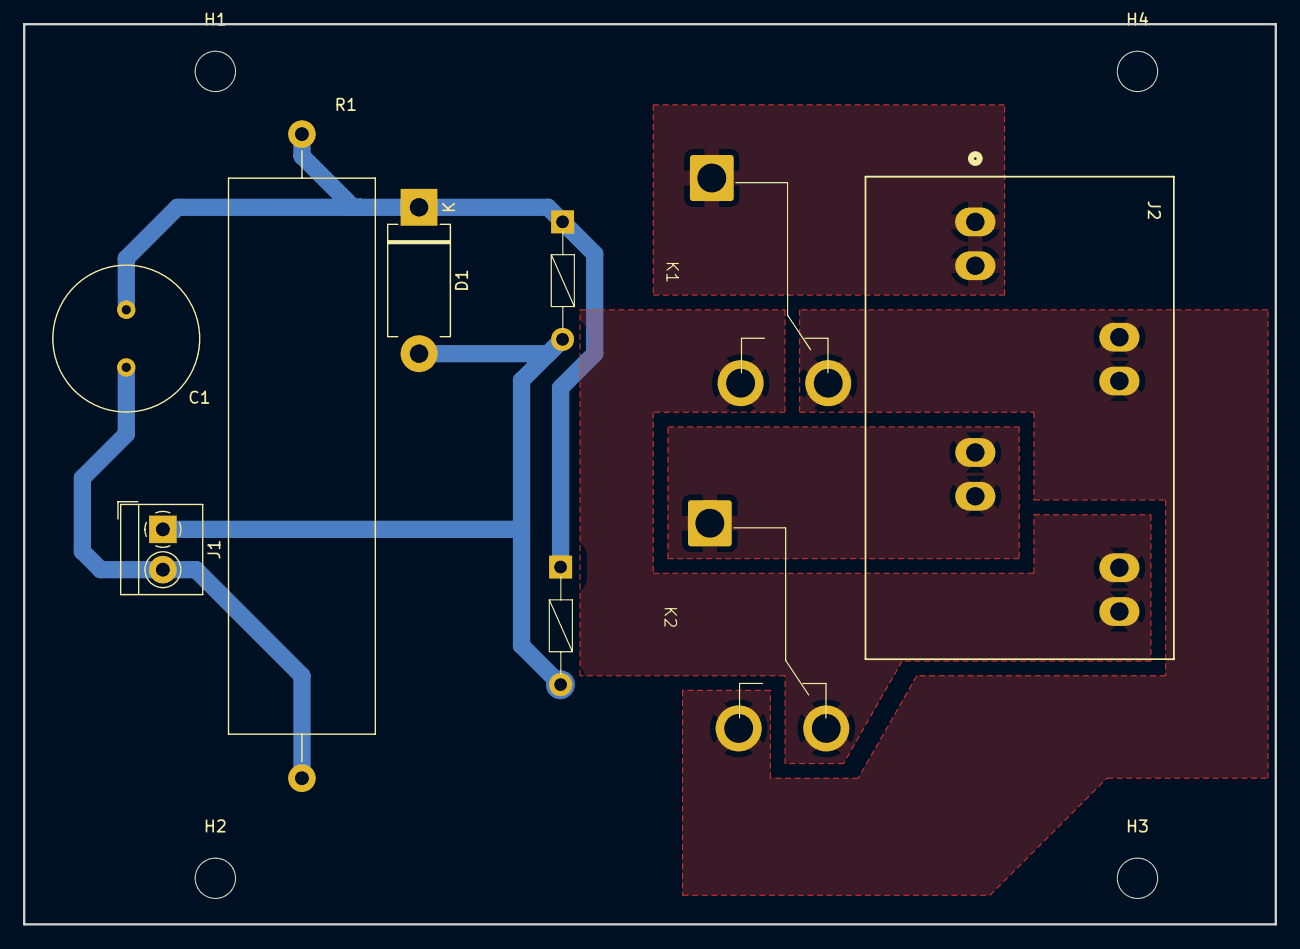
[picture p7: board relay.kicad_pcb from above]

Board: 2 copper layers, 108.6 x 78.1 mm, 11 parts (0 on the bottom side), 7 nets.

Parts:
C1: 100uF; C_Radial_D12.5mm_H25.0mm_P5.00mm
D1: D; D_DO-201AD_P12.70mm_Horizontal
H1, H2, H3, H4: MountingHole; MountingHole_3.5mm
J1: Screw_Terminal_01x02; TerminalBlock_4Ucon_1x02_P3.50mm_Horizontal
J2: Screw_Terminal_01x04; CONN_2453710000
K1, K2: J115F11CH24VDCS61.5U; SPDT-Relay-[J115F11CH24VDCS61.5U]
R1: 470; R_Axial_Power_L48.0mm_W12.5mm_P55.88mm

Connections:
/ENERGIZE: C1.2, J1.2, R1.2
CoilA: J2.3, K2.11
CoilB: J2.1, K1.11
Current In: J2.4, K1.12, K2.14
GND: D1.2 (A), J1.1, K1.A1, K2.A1
GNDD: J2.2, K1.14, K2.12
unnamed: C1.1, D1.1 (K), K1.A2, K2.A2, R1.1

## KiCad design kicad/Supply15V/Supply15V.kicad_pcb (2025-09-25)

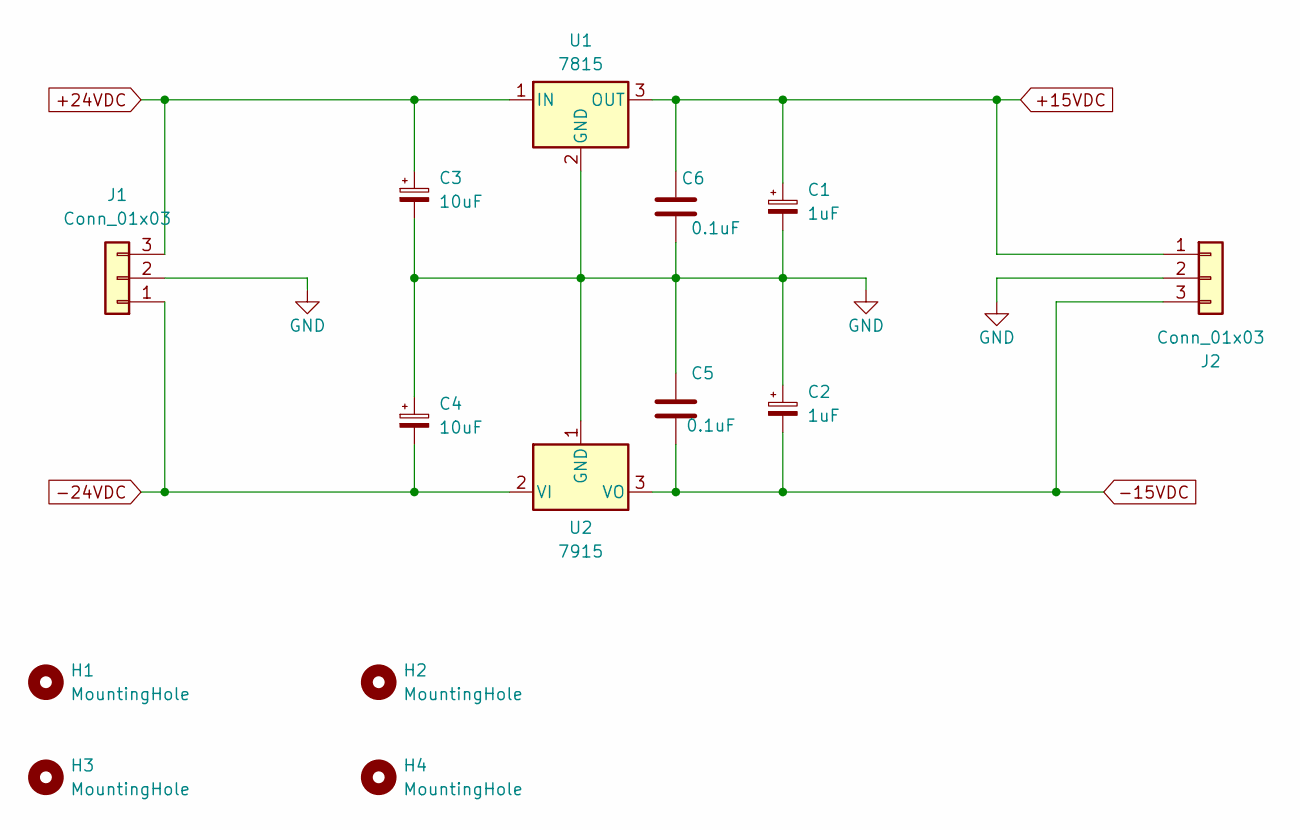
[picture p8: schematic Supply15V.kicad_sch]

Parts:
C1, C2: 1uF; CP_Radial_Tantal_D4.5mm_P2.50mm; MPN EEE-FK1H221P; DIGIKEY PARTNO PCE3812CT-ND
C3, C4: 10uF; CP_Radial_D5.0mm_P2.50mm; MPN EEE-FK1H221P; DIGIKEY PARTNO PCE3812CT-ND
C5, C6: 0.1uF; C_Disc_D4.3mm_W1.9mm_P5.00mm
H1, H2, H3, H4: MountingHole; MountingHole_4.3mm_M4_ISO7380
J1, J2: Conn_01x03; TerminalBlock_4Ucon_1x03_P3.50mm_Horizontal
U1: 7815; TO-220-3_Vertical
U2: 7915; TO-220-3_Vertical

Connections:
+15VDC: C1.1, C6.2, J2.1, U1.3 (OUT)
+24VDC: C3.1, J1.3, U1.1 (IN)
-15VDC: C2.2, C5.1, J2.3, U2.3 (VO)
-24VDC: C4.2, J1.1, U2.2 (VI)
GND: C1.2, C2.1, C3.2, C4.1, C5.2, C6.1, J1.2, J2.2, U1.2 (GND), U2.1 (GND)

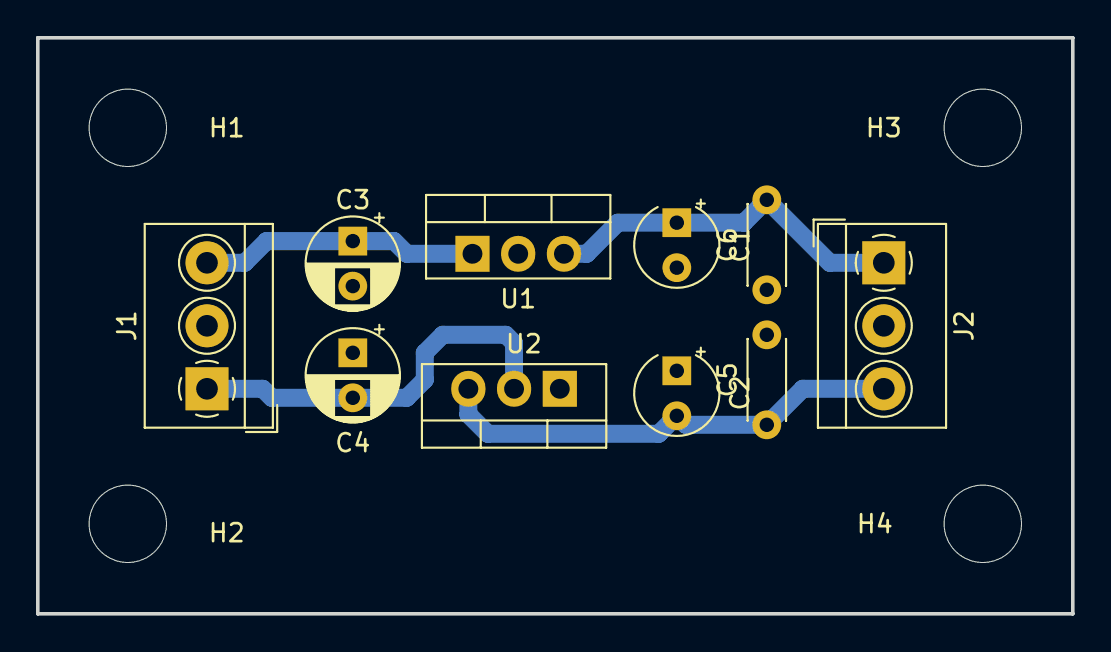
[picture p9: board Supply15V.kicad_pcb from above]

Board: 2 copper layers, 57.5 x 32.0 mm, 14 parts (0 on the bottom side), 5 nets.

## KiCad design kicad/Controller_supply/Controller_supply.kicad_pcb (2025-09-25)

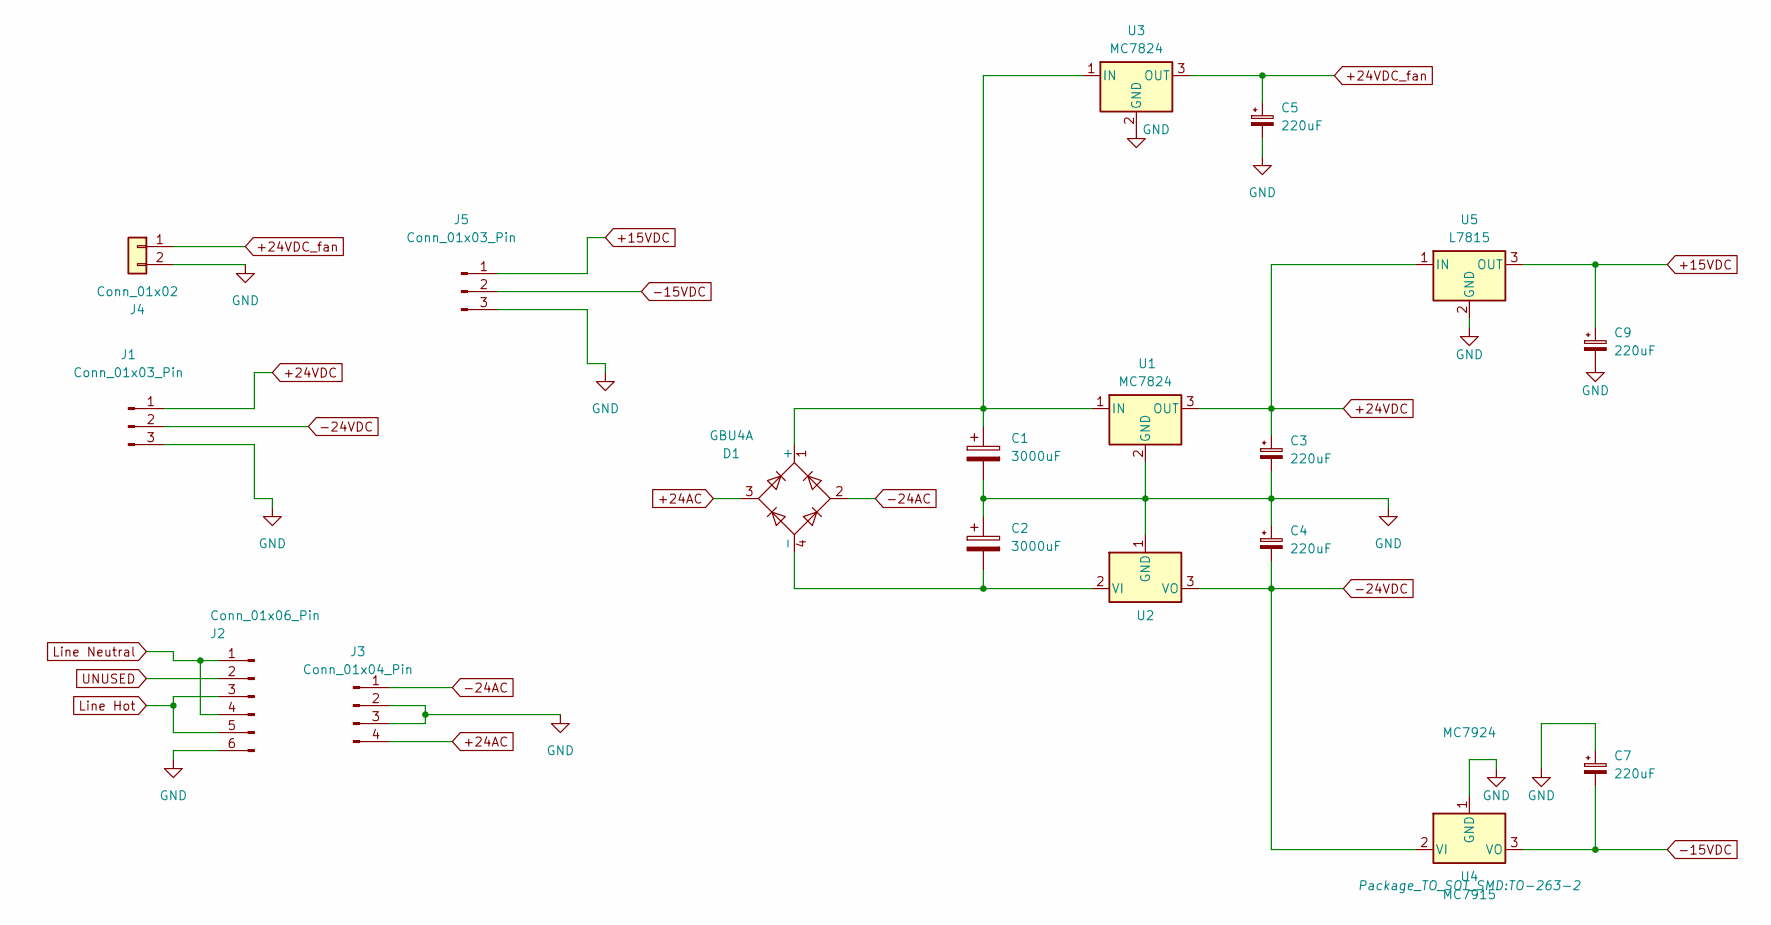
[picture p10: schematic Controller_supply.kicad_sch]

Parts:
C1, C2: 3000uF; CP_Elec_18x22; MPN EEE-FK1V302SV; DIGIKEY PARTNO P122523CT-ND
C3, C4, C5, C7, C9: 220uF; CP_Elec_10x10.5; MPN EEE-FK1H221P; DIGIKEY PARTNO PCE3812CT-ND
D1: GBU4A; Diode_Bridge_Vishay_GBU; MPN GBU4A; DIGIKEY PARTNO GBU4A-ND
J1, J5: Conn_01x03_Pin; PhoenixContact_GMSTBA_2,5_3-G-7,62_1x03_P7.62mm_Horizontal
J2: Conn_01x06_Pin
J3: Conn_01x04_Pin; Generic_pin-to-housing_1x04_P5.00mm_Horizontal
J4: Conn_01x02; Generic_7x7.5mm-footprt_1x02_P3.50mm_Horizontal
U1, U3: MC7824; TO-263-2; MPN MC7824CD2TR4G; DIGIKEY PARTNO MC7824CD2TR4GOSCT-ND
U2: MC7924; TO-263-2; MPN MC7924CD2TG; DIGIKEY PARTNO MC7924CD2TG-ND
U4: MC7915; TO-263-2
U5: L7815; TO-263-2

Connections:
+15VDC: C9.1, J5.1, U5.3 (OUT)
+24AC: D1.3, J3.4
+24VDC: C3.1, J1.1, U1.3 (OUT), U5.1 (IN)
+24VDC_fan: C5.1, J4.1, U3.3 (OUT)
-15VDC: C7.2, J5.2, U4.3 (VO)
-24AC: D1.2, J3.1
-24VDC: C4.2, J1.2, U2.3 (VO), U4.2 (VI)
GND: C1.2, C2.1, C3.2, C4.1, C5.2, C7.1, C9.2, J1.3, J2.6, J3.2, J3.3, J4.2, J5.3, U1.2 (GND), U2.1 (GND), U3.2 (GND), U4.1 (GND), U5.2 (GND)
unnamed: C1.1, D1.1 (+), U1.1 (IN), U3.1 (IN)
unnamed: C2.2, D1.4 (-), U2.2 (VI)
unnamed: J2.1, J2.4
unnamed: J2.3, J2.5

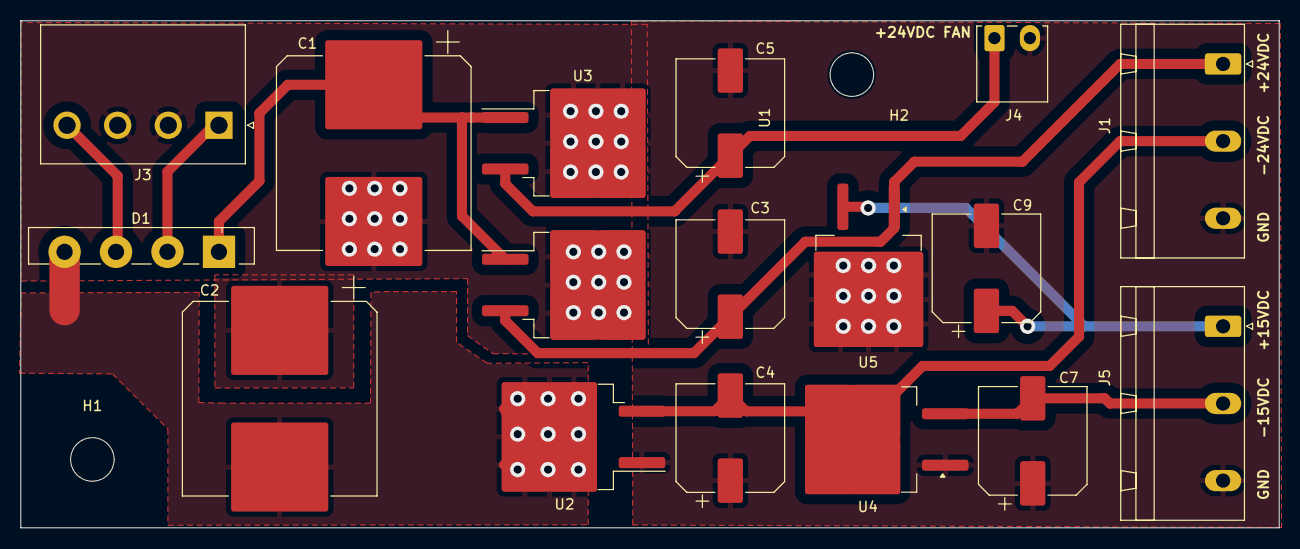
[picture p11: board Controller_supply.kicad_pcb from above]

Board: 2 copper layers, 124.3 x 50.1 mm, 19 parts (0 on the bottom side), 10 nets.

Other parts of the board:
H1, H2: MountingHole_4.3mm_M4

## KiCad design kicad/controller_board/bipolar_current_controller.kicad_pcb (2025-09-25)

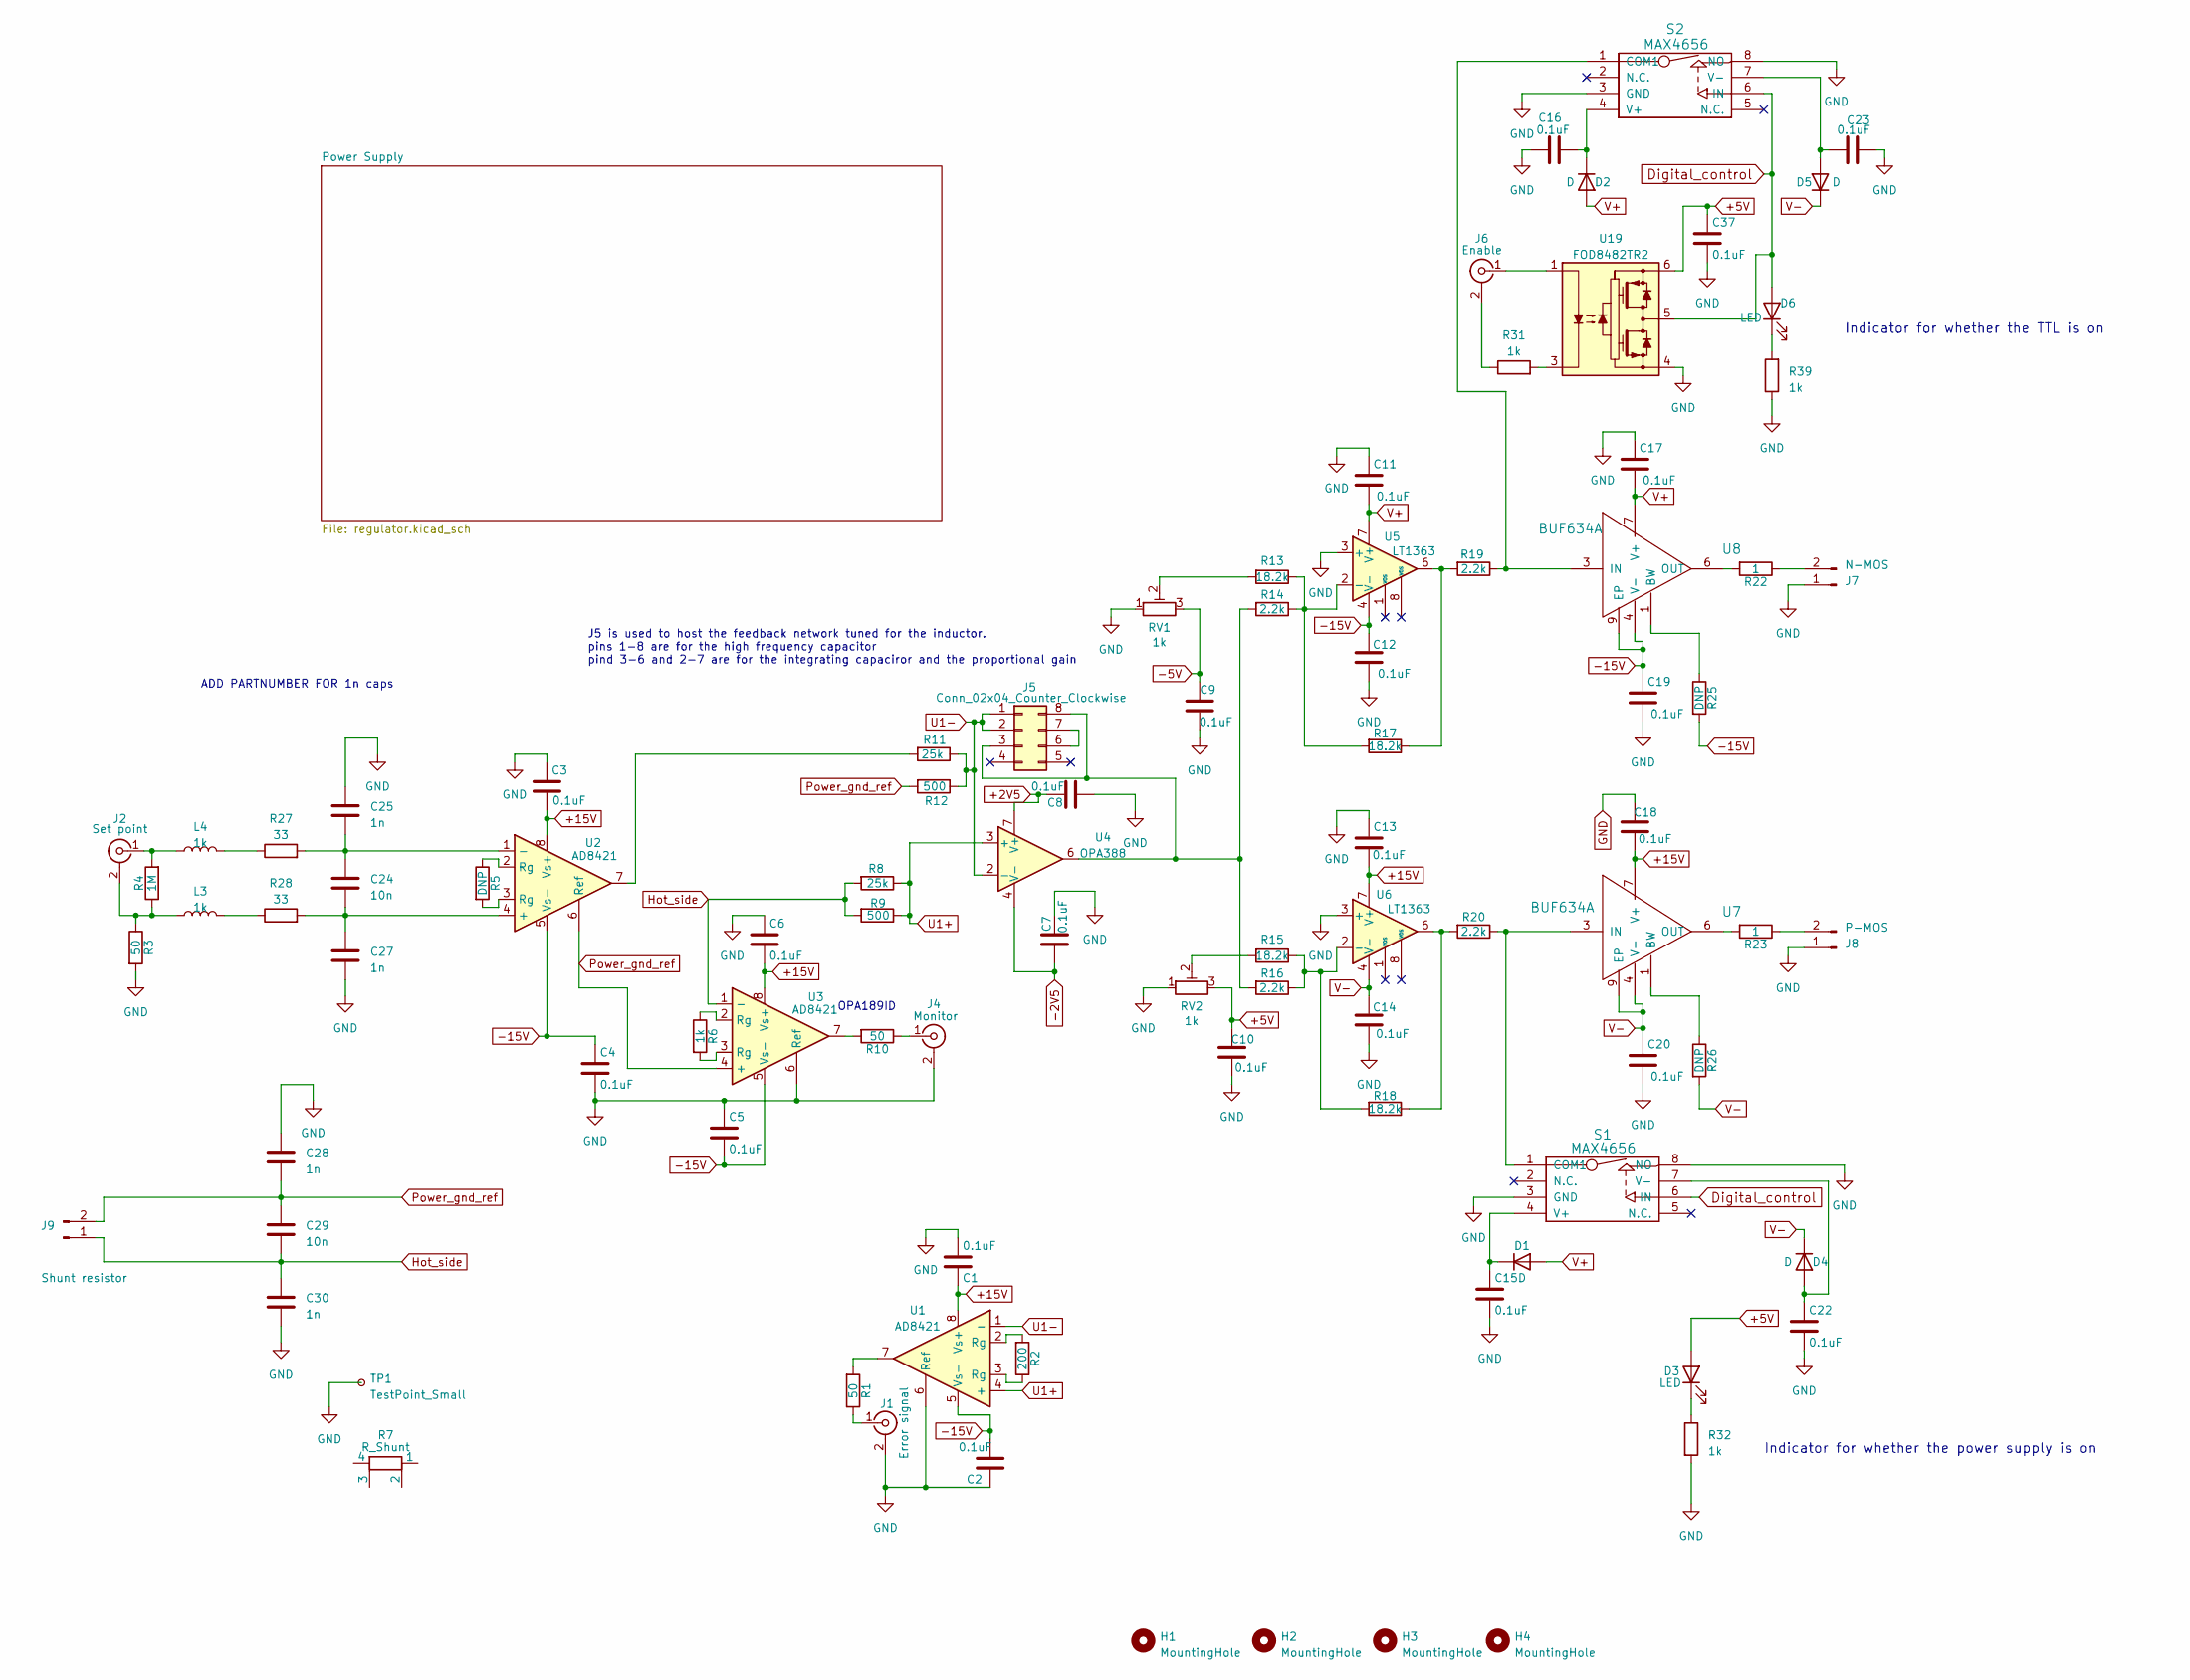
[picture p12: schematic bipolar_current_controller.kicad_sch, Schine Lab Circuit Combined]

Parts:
C1, C2, C3, C4, C5, C6, C7, C8, C9, C10, C11, C12, C13, C14, C15, C16, C17, C18, C19, C20, C22, C23, C37: 0.1uF; C_0603_1608Metric; MPN GCM188R71H104JA57D; DIGIKEY PARTNO 490-14357-1-ND
C24, C29: 10n; C_0603_1608Metric; MPN PARTNO C1608C0G1H103J080AA; DIGIKEY PARTNO 445-7404-1-ND
C25, C27, C28, C30: 1n; C_0603_1608Metric; MPN 1276-1018-1-ND; DIGIKEY PARTNO 1276-1018-1-ND
D1, D2, D4, D5: D; D_MiniMELF; MPN CLL4150 TR PBFREE; DIGIKEY PARTNO 1514-CLL4150TRPBFREECT-ND
D3, D6: LED; LED_D5.0mm_Horizontal_O3.81mm_Z3.0mm; MPN HLMP-4700-C0002; DIGIKEY PARTNO 516-2483-1-ND
H1, H2, H3, H4: MountingHole; MountingHole_4mm
J1: Error signal; BNC_Amphenol_B6252HB-NPP3G-50_Horizontal_mount_float; MPN 5227161-7; DIGIKEY PARTNO A32260-ND
J2: Set point; BNC_Amphenol_B6252HB-NPP3G-50_Horizontal_mount_float; MPN 5227161-7; DIGIKEY PARTNO A32260-ND
J4: Monitor; BNC_Amphenol_B6252HB-NPP3G-50_Horizontal_mount_float; MPN 5227161-7; DIGIKEY PARTNO A32260-ND
J5: Conn_02x04_Counter_Clockwise; SSO-8_7.62x10.1mm_P2.54mm_Clearance8mm; MPN 114-87-308-41-134161; DIGIKEY PARTNO 1212-1032-ND
J6: Enable; BNC_Amphenol_B6252HB-NPP3G-50_Horizontal_mount_float; MPN 5227161-7; DIGIKEY PARTNO A32260-ND
J7: N-MOS; Molex_KK-254_AE-6410-02A_1x02_P2.54mm_Vertical
J8: P-MOS; Molex_KK-254_AE-6410-02A_1x02_P2.54mm_Vertical
J9: Shunt resistor; Molex_KK-254_AE-6410-02A_1x02_P2.54mm_Vertical
L3, L4: 1k; L_0603_1608Metric; MPN MMZ1608R102ATA00; DIGIKEY PARTNO 445-MMZ1608R102ATA00CT-ND
R1, R3, R10: 50; R_0603_1608Metric; MPN FC0603E50R0BTBST1; DIGIKEY PARTNO 764-FC0603E50R0BTBST1CT-ND
R2: 200; R_0603_1608Metric; MPN RNCF0603TKY200R; DIGIKEY PARTNO RNCF0603TKY200RCT-ND
R4: 1M; R_0603_1608Metric; MPN RT0603BRD071ML; DIGIKEY PARTNO YAG4498CT-ND
R5: DNP; R_0805_2012Metric
R6: 1k; R_0805_2012Metric; MPN RNCF0805TKY1K00; DIGIKEY PARTNO RG2012V1.0KPCT-ND
R7: R_Shunt; MPN Y09430R01000F9L; DIGIKEY PARTNO 804-1050-ND
R8, R11: 25k; R_2512_6332Metric; MPN Y174525K0000T9R; DIGIKEY PARTNO 804-1122-1-ND
R9, R12: 500; R_2512_6332Metric; MPN Y1121500R000T9R; DIGIKEY PARTNO Y1121-500CT-ND
R13, R15, R17, R18: 18.2k; R_0805_2012Metric; MPN RK73H2ATTD1822F; DIGIKEY PARTNO 2019-RK73H2ATTD1822FCT-ND
R14, R16, R19, R20: 2.2k; R_0805_2012Metric; MPN MCU08050C2201FP500; DIGIKEY PARTNO 749-1728-1-ND
R22, R23: 1; R_0603_1608Metric; MPN RNCP0603FTD1R00; DIGIKEY PARTNO RNCP0603FTD1R00CT-ND
R25, R26: DNP; R_0603_1608Metric
R27, R28: 33; R_0603_1608Metric; MPN RC0603FR-0733RL; DIGIKEY PARTNO 311-33.0HRCT-ND
R31, R32, R39: 1k; R_0603_1608Metric; MPN RNCP0603FTD1K00; DIGIKEY PARTNO RNCP0603FTD1K00CT-ND
RV1, RV2: 1k; Potentiometer_Bourns_3296W_Vertical; MPN 3296W-1-102LF; DIGIKEY PARTNO 3296W-102LF-ND
S1, S2: MAX4656; MAX4656ESA+; MPN MAX4656ESA+; DIGIKEY PARTNO MAX4656ESA+-ND
TP1: TestPoint_Small; Laird_Technologies_BMI-S-210-F_44.00x30.50mm; MPN BMI-S-210-F and BMI-S-210-C; DIGIKEY PARTNO 903-1057-1-ND and 903-1020-ND
U1, U2, U3: AD8421; AD8421ARZ-R7; MPN AD8421ARZ-R7; DIGIKEY PARTNO AD8421ARZ-R7CT-ND
U4: OPA388; OPA388IDR; Partno MPN; DIGIKEY PARTNO 296-45348-1-ND
U5, U6: LT1363; LT1363CS8#TRPBF; MPN LT1363CS8#TRPBF; DIGIKEY PARTNO 505-LT1363CS8#TRPBFCT-ND
U7, U8: BUF634A; TI_SO-PowerPAD-8_ThermalVias; MPN BUF634AIDDAR; DIGIKEY PARTNO 296-BUF634AIDDARCT-ND
U19: FOD8482TR2; SSO-6_6.8x4.6mm_P1.27mm_Clearance8mm; MPN FOD8482TR2; DIGIKEY PARTNO 488-FOD8482TR2CT-ND

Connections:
+2V5: C8.2, U4.7 (V+); also elsewhere on the board
+5V: C10.2, C37.1, D3.2 (A), RV2.3, U19.6 (VCC); also elsewhere on the board
+15V: C1.1, C3.2, C6.2, C13.2, C18.2, U1.8 (Vs+), U2.8 (Vs+), U3.8 (Vs+), U6.7 (V+), U7.7 (V+); also elsewhere on the board
-2V5: C7.1, U4.4 (V-); also elsewhere on the board
-5V: C9.1, RV1.3; also elsewhere on the board
-15V: C2.2, C4.1, C5.2, C12.2, C19.1, R25.2, U1.5 (Vs-), U2.5 (Vs-), U3.5 (Vs-), U5.4 (V-), U8.4 (V-), U8.9 (EP); also elsewhere on the board
Digital_control: D6.2 (A), S1.6 (IN), S2.6 (IN), U19.5 (VO)
GND: C1.2, C2.1, C3.1, C4.2, C5.1, C6.1, C7.2, C8.1, C9.2, C10.1, C11.1, C12.1, C13.1, C14.1, C15.2, C16.1, C17.1, C18.1, C19.2, C20.2, C22.2, C23.1, C25.1, C27.2, C28.1, C30.2, C37.2, J1.2 (Ext), J4.2 (Ext), J7.1, J8.1, R3.2, R32.2, R39.1, RV1.1, RV2.1, S1.3 (GND), S1.8 (NO), S2.3 (GND), S2.8 (NO), TP1.1, U1.6 (Ref), U3.6 (Ref), U5.3 (+), U6.3 (+), U19.4 (VEE); also elsewhere on the board
Hot_side: C29.2, C30.1, J9.1, R8.2, R9.2, U3.1 (-)
unnamed: C15.1, D1.1 (K), S1.4 (V+)
unnamed: C16.2, D2.1 (K), S2.4 (V+)
unnamed: D3.1 (K), R32.1
unnamed: C22.1, D4.2 (A), S1.7 (V-)
unnamed: C23.2, D5.2 (A), S2.7 (V-)
unnamed: D6.1 (K), R39.2
unnamed: J1.1 (In), R1.1
unnamed: J2.2 (Ext), L3.1, R3.1, R4.1
unnamed: J2.1 (In), L4.1, R4.2
unnamed: J4.1 (In), R10.1
unnamed: J5.3, J5.8, R14.2, R16.2, U4.6
unnamed: J5.6, J5.7
unnamed: J6.2 (Ext), R31.1
unnamed: J6.1 (In), U19.1 (A)
unnamed: J7.2, R22.1
unnamed: J8.2, R23.1
unnamed: L3.2, R28.1
unnamed: L4.2, R27.1
unnamed: R1.2, U1.7
unnamed: R2.1, U1.3 (Rg)
unnamed: R2.2, U1.2 (Rg)
unnamed: R5.1, U2.2 (Rg)
unnamed: R5.2, U2.3 (Rg)
unnamed: R6.1, U3.2 (Rg)
unnamed: R6.2, U3.3 (Rg)
unnamed: R10.2, U3.7
unnamed: R11.2, U2.7
unnamed: R13.2, RV1.2
unnamed: R15.2, RV2.2
unnamed: R17.1, R19.2, U5.6
unnamed: R18.1, R20.2, U6.6
unnamed: R20.1, S1.1 (COM1), U7.3 (IN)
unnamed: R19.1, S2.1 (COM1), U8.3 (IN)
unnamed: C24.2, C27.1, R28.2, U2.4 (+)
unnamed: C24.1, C25.2, R27.2, U2.1 (-)
unnamed: R13.1, R14.1, R17.2, U5.2 (-)
unnamed: R15.1, R16.1, R18.2, U6.2 (-)
unnamed: R26.1, U7.1 (BW)
unnamed: R23.2, U7.6 (OUT)
unnamed: R25.1, U8.1 (BW)
unnamed: R22.2, U8.6 (OUT)
unnamed: R31.2, U19.3 (C)
Power_gnd_ref: C28.2, C29.1, J9.2, R12.2, U2.6 (Ref), U3.4 (+)
U1+: R8.1, R9.1, U1.4 (+), U4.3 (+)
U1-: J5.1, J5.2, R11.1, R12.1, U1.1 (-), U4.2 (-)
V+: C11.2, C17.2, D1.2 (A), D2.2 (A), U5.7 (V+), U8.7 (V+); also elsewhere on the board
V-: C14.2, C20.1, D4.1 (K), D5.1 (K), R26.2, U6.4 (V-), U7.4 (V-), U7.9 (EP); also elsewhere on the board

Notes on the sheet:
J5 is used to host the feedback network tuned for the inductor. pins 1-8 are for the high frequency capacitor pind 3-6 and 2-7 are for the integrating capaciror and the proportional gain
ADD PARTNUMBER FOR 1n caps
Indicator for whether the TTL is on
Indicator for whether the power supply is on
OPA189ID


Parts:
C31, C32: 220uF; CAP_polar_220uF; MPN EEE-FK1V221AP; DIGIKEY PARTNO PCE4428CT-ND
C33, C34, C39, C40, C49, C51: 10uF; C_1210_3225Metric; MPN C3225X7R1H106M250AC; DIGIKEY PARTNO 445-14933-1-ND
C35, C36: 47uF; CP_EIA-7343-43_Kemet-X; MPN T495X476K035ATE300; DIGIKEY PARTNO 399-3905-1-ND
C41, C42, C45, C46: 0.33uF; C_0603_1608Metric; MPN C1608X7R1H334K080AC; DIGIKEY PARTNO 445-5950-1-ND
C43, C44, C47, C48: 0.1uF; C_0603_1608Metric; MPN GCM188R71H104JA57D; DIGIKEY PARTNO 490-14357-1-ND
C50, C52: 1uF; CP_EIA-3528-21_Kemet-B; MPN T491B105K050AT; DIGIKEY PARTNO 399-9720-1-ND
L1, L2: 100uH; L_TDK_SLF10145; MPN SLF10145T-101M1R0-PF; DIGIKEY PARTNO 445-1976-1-ND
P1: CONN_01X03; Conn_01X03-3.5mm; MPN 1984620; DIGIKEY PARTNO 277-1722-ND
R33, R34: 1.8k; R_0603_1608Metric; MPN PTN0603E1801BST1; DIGIKEY PARTNO 764-1393-1-ND
R35, R36, R37, R38: 120; R_0603_1608Metric; MPN RG1608P-121-B-T5; DIGIKEY PARTNO RG16P120BCT-ND
R40, R41: 30m; R_1206_3216Metric; MPN D1WEL1206MR033F-T5; DIGIKEY PARTNO 4463-D1WEL1206MR033F-T5CT-ND
U11: LM338; TO-220-3_Vertical; MPN LM338T/NOPB; DIGIKEY PARTNO LM338T/NOPB-ND
U12: LM337_TO220; TO-220-3_Vertical; MPN LM337SP; DIGIKEY PARTNO 497-1585-5-ND
U13: LM7915; TO-263-2; MPN MC7915ACD2TG; DIGIKEY PARTNO MC7915ACD2TGOS-ND
U14: uA7815; TO-252-2; MPN BA7815FP-E2; DIGIKEY PARTNO BA7815FP-E2CT-ND
U15: LM7905; TO-263-2; MPN L7905CD2T-TR; DIGIKEY PARTNO 497-1214-1-ND
U16: LM7805; TO-263-3_TabPin2; MPN UA7805CKTTR; DIGIKEY PARTNO 296-20796-1-ND
U17: TL1963A; TL1963ADCQR; MPN TL1963ADCQR; DIGIKEY PARTNO 296-25119-1-ND
U18: LM337_TO220; TO-263-3_TabPin2; MPN LM337KTTR; DIGIKEY PARTNO 296-20746-1-ND

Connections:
+2V5: C51.1, U17.4 (OUT), U17.5 (ADJ); also elsewhere on the board
+5V: C47.1, C49.1, U16.3 (OUT), U17.1 (~SHDN), U17.2 (IN); also elsewhere on the board
+15V: C43.1, C45.1, U14.3 (OUT), U16.1 (IN); also elsewhere on the board
+24V: C31.1, C33.1, L1.1, P1.1
-2V5: C52.2, R37.2, U18.3 (VO); also elsewhere on the board
-5V: C48.2, C50.2, U15.3 (OUT), U18.2 (VI); also elsewhere on the board
-15V: C44.2, C46.2, U13.3 (OUT), U15.2 (IN); also elsewhere on the board
-24V: C32.2, C34.2, L2.1, P1.3
GND: C31.2, C32.1, C33.2, C34.1, C35.2, C36.1, C41.2, C42.1, C43.2, C44.1, C45.2, C46.1, C47.2, C48.1, C49.2, C50.1, C51.2, C52.1, P1.2, R33.2, R34.1, R36.1, R40.2, R41.1, U13.1 (GND), U14.2 (GND), U15.1 (GND), U16.2 (GND), U17.3 (GND), U17.6 (GND); also elsewhere on the board
unnamed: C39.2, R40.1
unnamed: C40.1, R41.2
unnamed: R33.1, R38.2, U11.1 (ADJ)
unnamed: C35.1, L1.2, U11.3 (VI)
unnamed: R34.2, R35.1, U12.1 (ADJ)
unnamed: C36.2, L2.2, U12.2 (VI)
unnamed: R36.2, R37.1, U18.1 (ADJ)
V+: C39.1, C41.1, R38.1, U11.2 (VO), U14.1 (IN); also elsewhere on the board
V-: C40.2, C42.2, R35.2, U12.3 (VO), U13.2 (IN); also elsewhere on the board


Board: 4 copper layers, 114.3 x 127.0 mm, 130 parts (0 on the bottom side), 65 nets.

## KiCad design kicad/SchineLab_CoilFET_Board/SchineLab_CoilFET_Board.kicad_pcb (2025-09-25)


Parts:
C1, C2: 0.1uF; C_0603_1608Metric; MPN C0603C104J5RACAUTO; DIGIKEY PARTNO 399-6853-1-ND
C3, C4: UKL1J102KHD; CAP_UBY_18X35P5_NCH
H1, H2, H3, H4: MountingHole; MountingHole_4mm
J3: SENSE; PinHeader_1x02_P2.54mm_Vertical
J4: N-MOS; PinHeader_1x02_P2.54mm_Vertical
J8: P-MOS; PinHeader_1x02_P2.54mm_Vertical
J9: 2491920000; CONN_249192
Q1: Q_NMOS_GDS; PowerMOS; DIGIKEY PARTNO IXFN520N075T2-ND
Q2: Q_PMOS_GDS; PowerMOS; DIGIKEY PARTNO IXTN170P10P-ND
R1, R2: 20; R_0603_1608Metric_Pad0.98x0.95mm_HandSolder; DIGIKEY PARTNO P20.00BYCT-ND
R9: R_Shunt; SIP-4-ShuntResistor-Riedon

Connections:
+HCC: C1.1, C3.1, J9.5, J9.6, J9.7, J9.8, Q1.2 (D)
-HCC: C2.2, C4.2, J9.13, J9.14, J9.15, J9.16, Q2.2 (D)
GND: C1.2, C2.1, C3.2, C4.1, J4.1, J8.1, J9.17, J9.18, J9.19, J9.20, R9.4
Load_hot: J9.9, J9.10, J9.11, J9.12, Q1.3 (S), Q2.3 (S)
unnamed: J3.1, R9.2
unnamed: J3.2, R9.3
unnamed: J4.2, R1.2
unnamed: J8.2, R2.2
unnamed: Q1.1 (G), R1.1
unnamed: Q2.1 (G), R2.1
load_cold: J9.1, J9.2, J9.3, J9.4, R9.1



Board: 2 copper layers, 200.0 x 127.0 mm, 17 parts (11 on the bottom side), 11 nets.

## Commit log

2025-05-27 Final Board schematics and layouts, Also added custom footprints that were made for the relay and terminal connector block.
    [H_bridge.kicad_pcb, H_bridge.kicad_sch, Supply15V.kicad_pcb, Supply15V.kicad_sch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]
2026-06-17 Irrelevant files removed
    [H-bridge.kicad_pcb, H-bridge.kicad_sch, Unipolar_FET_Board.kicad_pcb, Unipolar_FET_Board.kicad_sch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]
2026-06-17 Update README for project name and circuit details
